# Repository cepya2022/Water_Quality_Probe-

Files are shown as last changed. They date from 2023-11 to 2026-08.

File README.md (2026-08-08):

# Water_Quality_Probe-

## Introduction

The development of open-source code and hardware instruments enables both the creation of new technologies and the redesign and adaptation of existing instruments to the user's specific needs. This allows free access to design and operational documentation, creating the possibility for the developed instruments to be replicated, assembled, studied, modified, shared, and collaboratively commercialized by anyone.

The current project involves the design of a low-cost multiparametric water quality probe that enables in situ and remote sensing of physicochemical variables relevant to the environment, such as conductivity, dissolved oxygen, temperature, and pH in bodies of water. The first prototype based on Arduino is already available, and efforts are underway to refine it in order to achieve a more robust, economical, and efficient product. This project proposes integrating the microcontroller into a single printed circuit board (PCB) that facilitates data acquisition and storage over extended periods, reduces energy consumption, and enhances robustness, considering its predominantly outdoor operation.

<p>
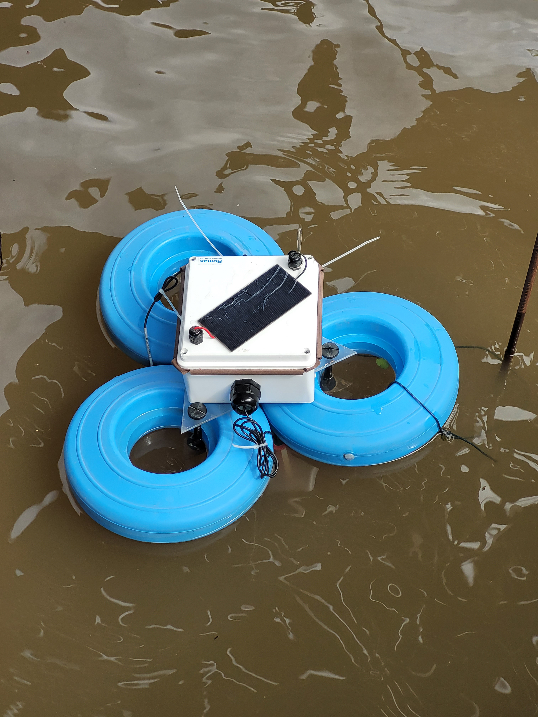
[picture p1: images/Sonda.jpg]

</p>

### Hardware

The monitoring station consists of a sealed waterproof box that floats with the assistance of auxiliary buoys. Inside the box, there is an Arduino Mega microcontroller connected to an external clock, an SD memory module, a low-energy Bluetooth module, a solar-powered energy system, and signal processing and decoupling systems for each sensor. Submersible cables extend from this box to the probes, allowing sampling in the water.

Regarding energy aspects, a solar-powered system was designed. It includes a Li-Ion battery (or two arranged in parallel) that powers the microcontroller and sensors, connected to a 1 Watt solar panel, providing indefinite energy autonomy.

Additionally, it integrates a Bluetooth device using 4.0 BLE (Bluetooth Low Energy) technology. The Serial Bluetooth Terminal® app enables remote control of the probe, such as remote power on/off, selection of measurement intervals, sensor calibration, and data query, curing, and collection. It's worth noting that each measurement includes the exact date and time it was taken. These features make it easy to remotely monitor many relevant variables over extended periods with high sampling rates, allowing for detailed time-series data collection at the study site.

<p align="center">
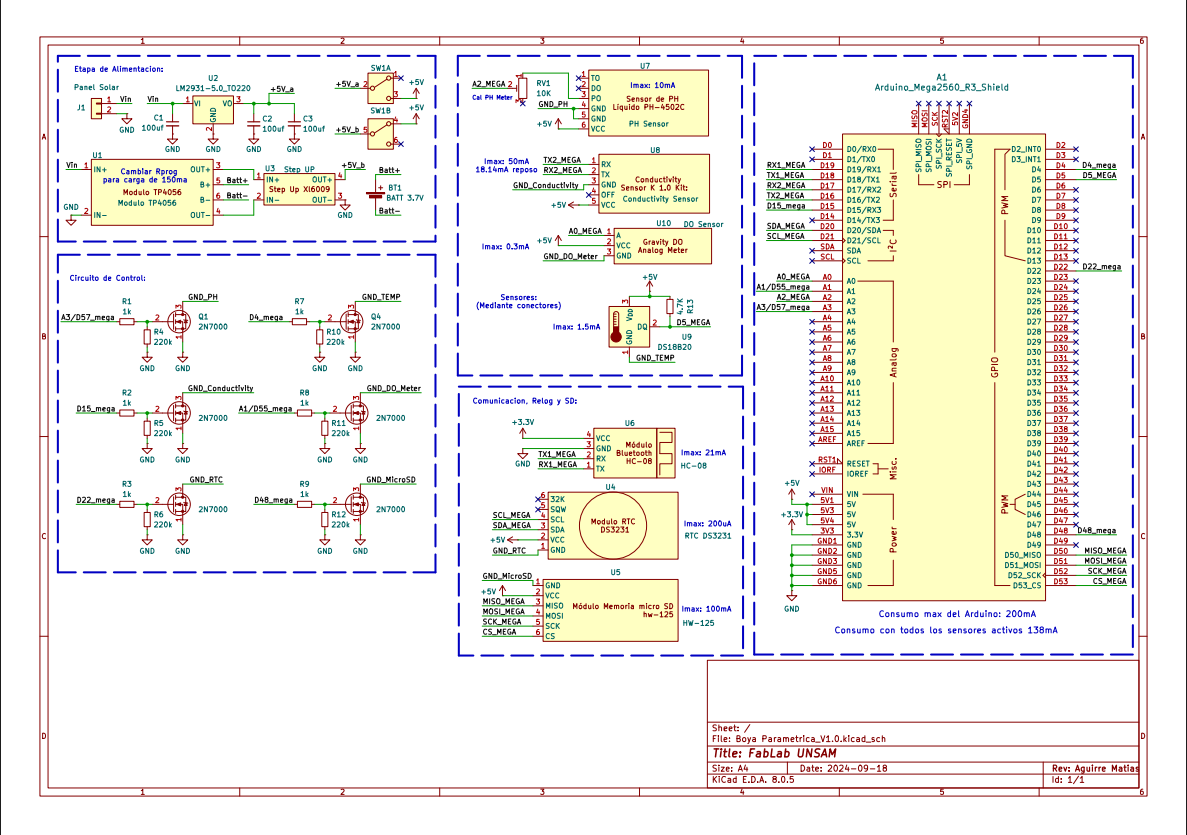
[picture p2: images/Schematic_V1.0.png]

</p>

#### Components

* Solar Panel
* Double battery holder
* Arduino Mega 2560 Rev3
* Step Up Power Supply Xl6009 Dc Adjustable Dc 5v 35v 3a Max Arduino
* Lithium Battery Charger Micro USB Module Tp4056 5v
* HC-08 BLE Bluetooth Module
* Micro SD Memory Reader Module: hw-125
* DS3231 RTC Clock
* DS18B20 Submersible Stainless Steel Digital Temperature Sensor
* PH-4502C Liquid PH Sensor with E201-BNC Electrode
* Conductivity Sensor Conductivity K 1.0 Kit (Atlas Scientific)
* Gravity™ Analog Dissolved Oxygen Meter Dissolved Oxygen Sensor (Atlas Scientific)
* 6x 2N7000 N-Channel MOSFETs (low-side power switching, one per module)
* Resistors (1 kΩ gate series, 220 kΩ gate pull-down, 1.7 kΩ OneWire pull-up)

Each sensor and peripheral (pH, conductivity, dissolved oxygen, temperature, RTC and SD card) has
its ground routed through its own 2N7000 MOSFET, so the microcontroller can power each module
independently. Driving the corresponding gate pin `HIGH` closes the low-side switch and powers the
module; `LOW` removes its ground reference and turns it off. Earlier prototypes used an
optocoupled relay module for this; the V1.0 PCB replaced it entirely with MOSFETs.

### Software

The research team is continuosly working on and improving the code. It is written in c++ programming language inside the Arduino IDE as it is the default language for arduino microcontrollers. The system was design to enter sleep mode inside the loop function while the `measurement` option is disabled or in between measurements. It includes an interruption function which is activated once a message is received via Bluetooth. This function wakes the system, executes the corresponding command and once it is finished, it enters the loop again. The different commands include turning on/off the measurement cycle and setting its frequency, sensor calibration, data query and current state information. The updated code is available [here](https://github.com/cepya2022/Water_Quality_Probe-/blob/main/Code_Water_Quality_Probe.ino).

#### Building the firmware

Target board: **Arduino Mega 2560**.

⚠️ **`do_grav.h` is not included in this repository**, so the sketch will not compile from a fresh
clone until the library that provides it is installed. It comes from Atlas Scientific's
**`atlas_gravity`** library (the `Gravity_DO` class used for the dissolved oxygen sensor). That
library is not published to the Arduino Library Manager — download it from Atlas Scientific's
GitHub and copy the `atlas_gravity` folder into your Arduino `libraries/` directory manually.

The following libraries are also required. All except `atlas_gravity` are available through the
Arduino IDE Library Manager:

| Library | Used for |
|---|---|
| `atlas_gravity` | dissolved oxygen sensor (`do_grav.h`) — **manual install, see above** |
| `RTClib` | DS3231 real time clock |
| `Low-Power` | sleep between measurements |
| `DallasTemperature` | DS18B20 temperature sensor |
| `OneWire` | DS18B20 bus |
| `Wire` | I²C (RTC) — bundled with the IDE |
| `SPI` | SD card bus — bundled with the IDE |
| `SD` | SD card — bundled with the IDE |

The conductivity module is driven over `Serial2` with plain text commands, so it needs no library.

Setting the clock: `corregirReloj()` is called from `setup()` but is left commented out. Uncomment
it, upload once while connected to a computer so the RTC picks up the compile-time timestamp, then
comment it out again and re-upload — otherwise the clock is reset to the compile time on every boot.

#### Measurement cycles

Once the measurment is set to `On`, the interface will ask the user to identify the location with an ID (`locationID`) which must be a number. Once it is provided, the arduino will save the `On` state along with the location ID and the current frequency (default is 15 seconds), in a .txt file inside the SD Card. This feature acts as a reassurance in case of a sudden shutdown and restart of the system or any kind of reboot. In this case, during the setup function of the arduino, this file is checked to seek the last state in which the system was operating. In case the measurement was `On`, it sets the frequency and the location ID to their previous states and starts the measurement cycle, otherwise it keeps the default values and enters the loop. The frequency intervals available in the current version are 15 seconds and 1, 5, 15 or 30 minutes. Usually, for outdoor measurements, 30 minutes is a reasonable interval considering battery consumption, solar exposure and a relatively high sampling rate compared to other sampling methods.

During the measurement cycle, the arduino powers each sensor on and off in turn, so that only the module being read draws current at any given moment. First it turns on the pH sensor (`pH`) and waits about 2 seconds for it to settle, then averages 10 consecutive analog samples taken 10 ms apart and converts that average to a pH value using the stored calibration line. Next is the temperature sensor (`T`), which is read once. Third is the conductivity sensor (`EC`), one of the most accurate and precise ones and the slowest per reading, so a single measurement is taken; the value returned by the module is temperature-compensated, which is why it must be read after the temperature. Along with conductivity, the module also returns total dissolved solids (`TDS`). Finally, the dissolved oxygen (`DO`) is read once. Once the parameters are measured, the current date and time are read from the RTC and the record is appended to a .txt file on the SD card as semicolon-separated values, in the order: `date`;`time`;`DO`;`EC`;`TDS`;`pH`;`T`;`locationID`.

> Note: earlier revisions of this document described a 3 minute pH stabilization wait, attributed to
> induction from the relay module, and a 10-reading average for every sensor. Both belong to the
> relay-based prototype and do not describe the current firmware — the V1.0 board has no relays, and
> only pH averages multiple samples. The paragraph above reflects what the code actually does.

#### Data query and state info

There are 3 types of data querys available. The first to refer to the data stored from the measurement cycles. One of them returns the entire information stored in the SD card inside the measurement file, while the other returns only the new information added since the last measurement data query. In case of a shutdown and restart of the system or any kind of reboot, the pointer of the file returns to the first line of the text file, so both queries will return the same information. The third type of data query refers to individual measurements of each sensor taken at real-time. This includes options for each of the 4 sensors and the RTC clock.

The current state information is also a query that returns wether the the measurement mode is On or Off, and the established frequency.

#### Sensor Calibration

The only sensor without the need of a calibration process is the Temperature one, the other three sensors have specific code and procedures for their correct calibrations. 

For the pH sensor, the calibration requires a pH=7 and a pH=4 standard solutions. First, the interface will request the user to use the pH=7 solution and press the `Ok` command when a stable condition is reached. It is recommended to wait at least 3 minutes until it reaches a stable electronic condition in each solution. Then, it will request to do the same in the pH=4 solution. Make sure to wash the probe with distilled water in between solutions. Once both solutions are used, the arduino will give the user the notification that the pH sensor is calibrated and it will save the calibration curve parameters, slope of curve (m) and intercept to the origin (O.o.), in the same file as the Location ID and the measurement state for it to be used in case of a sudden shutdown and restart of the system or any kind of reboot.

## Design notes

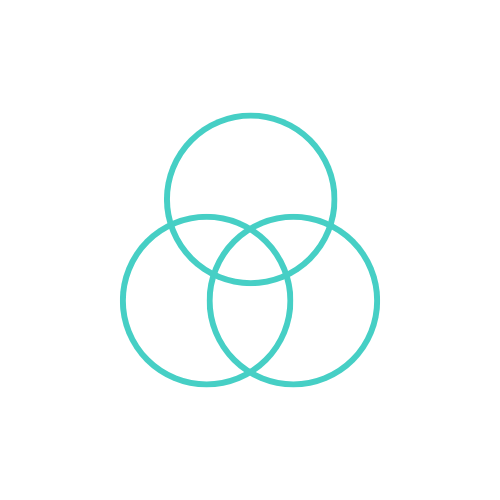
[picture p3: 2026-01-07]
flutter-app/assets/images/bg-w_no_sensa.png

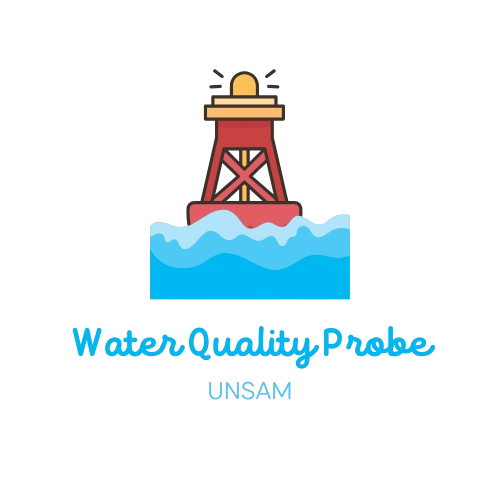
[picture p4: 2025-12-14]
flutter-app/flutter-app/assets/images/Water_Quality_Probe.png

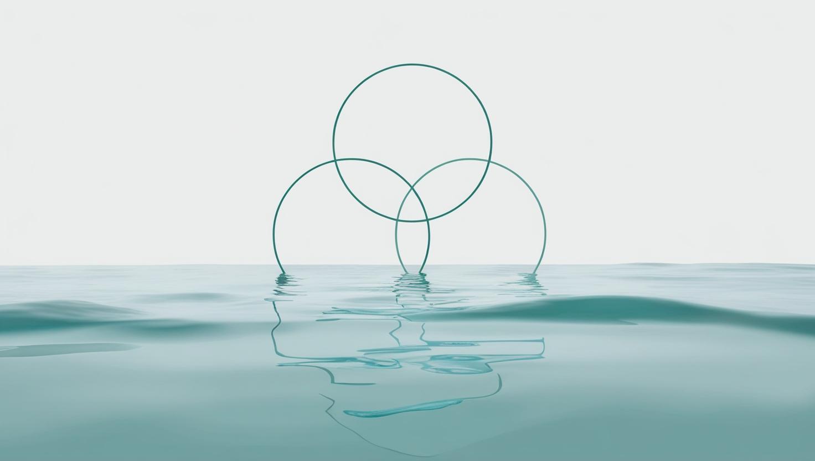
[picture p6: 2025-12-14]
flutter-app/assets/images/Circulos.jpg

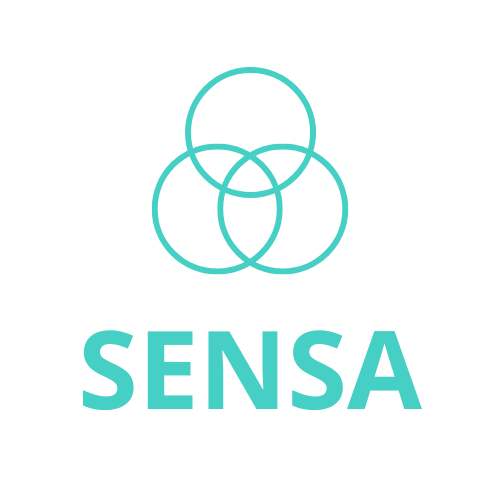
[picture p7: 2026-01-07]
flutter-app/assets/images/bg-w_sensa.png

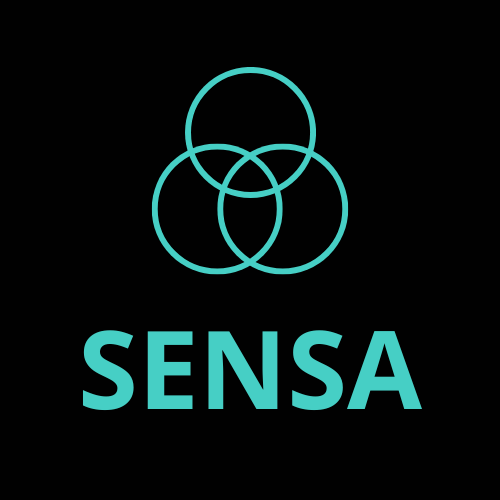
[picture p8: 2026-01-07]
flutter-app/assets/images/bg-b_sensa.png

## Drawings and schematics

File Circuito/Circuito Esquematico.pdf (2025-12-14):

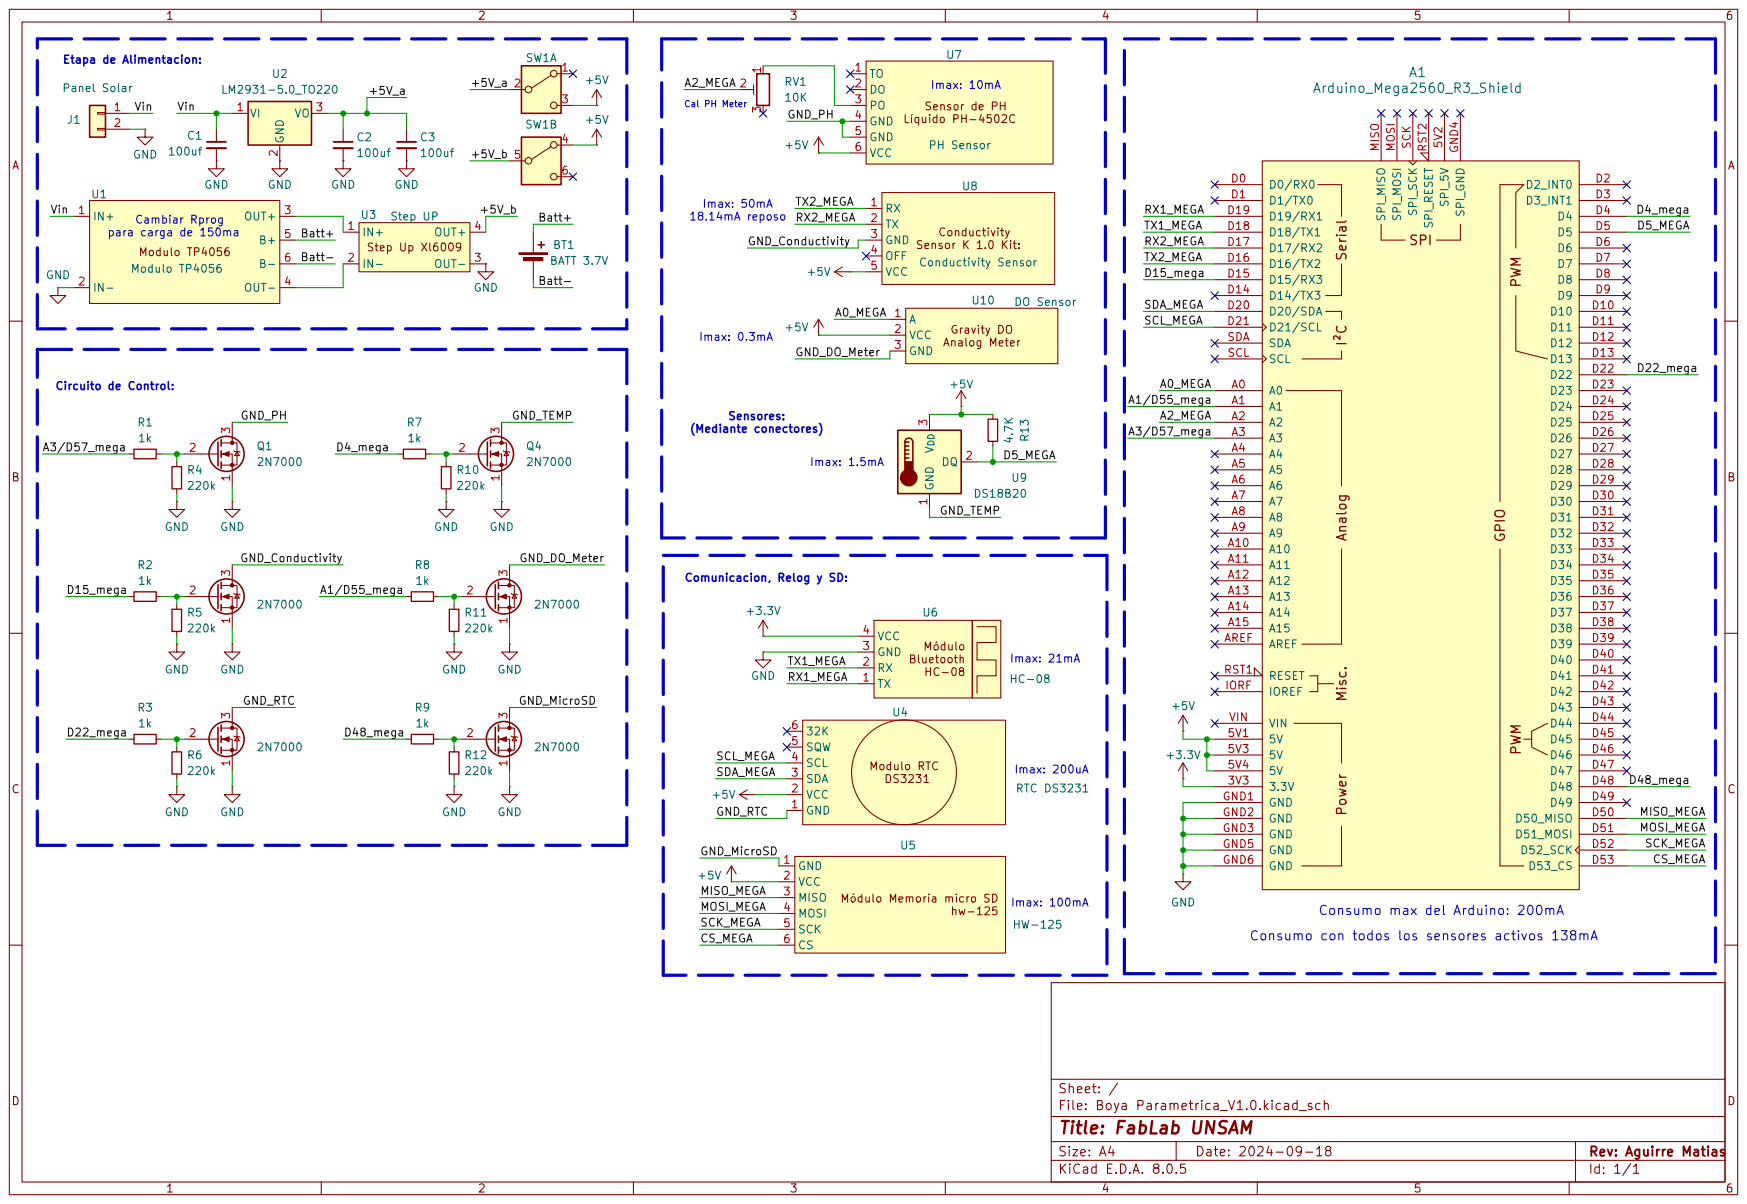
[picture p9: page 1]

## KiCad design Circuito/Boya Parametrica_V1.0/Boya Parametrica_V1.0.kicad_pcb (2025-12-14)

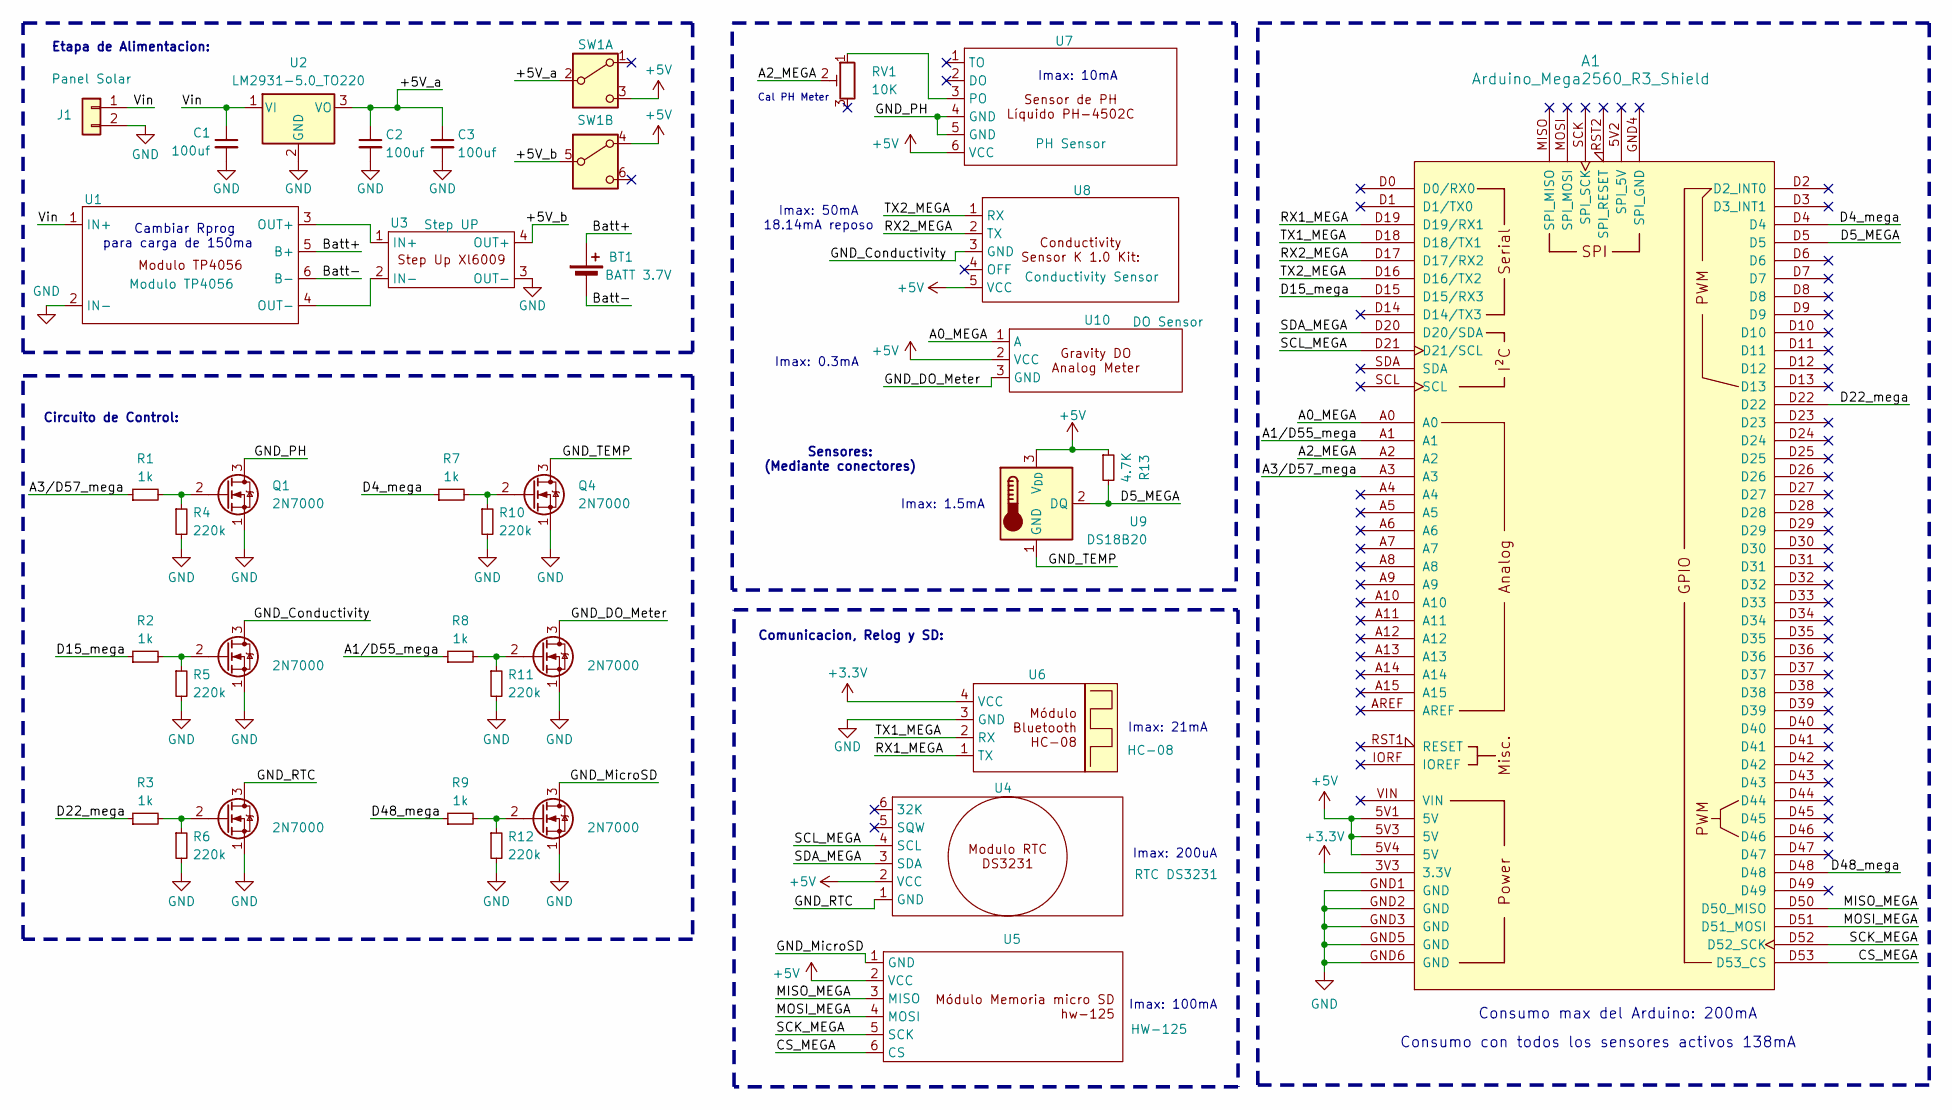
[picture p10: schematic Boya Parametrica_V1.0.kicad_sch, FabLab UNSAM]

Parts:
A1: Arduino_Mega2560_R3_Shield
BT1: BATT 3.7V; JST_EH_B2B-EH-A_1x02_P2.50mm_Vertical
C1, C2, C3: 100uf; C_Disc_D3.8mm_W2.6mm_P2.50mm
J1: Panel Solar; TerminalBlock_bornier-2_P5.08mm
Q1, Q2, Q3, Q4, Q5, Q6: 2N7000; TO-92L_Wide
R1, R2, R3, R7, R8, R9: 1k; R_Axial_DIN0204_L3.6mm_D1.6mm_P5.08mm_Horizontal
R4, R5, R6, R10, R11, R12: 220k; R_Axial_DIN0204_L3.6mm_D1.6mm_P5.08mm_Horizontal
R13: 4.7K; R_Axial_DIN0204_L3.6mm_D1.6mm_P5.08mm_Horizontal
RV1: 10K; Potentiometer_Bourns_3296W_Vertical
SW1: SW_CK_JS202011AQN_DPDT_Angled
U1: Modulo TP4056; TP4056-18650
U2: LM2931-5.0_TO220; TO-220-3_Vertical
U3: Step UP; hw-045
U4: RTC DS3231; RTC_DS3231
U5: HW-125; MICRO SD CARD HW-125
U6: HC-08; JST_EH_B4B-EH-A_1x04_P2.50mm_Vertical
U7: PH Sensor; JST_EH_B6B-EH-A_1x06_P2.50mm_Vertical
U8: Conductivity Sensor; JST_EH_B5B-EH-A_1x05_P2.50mm_Vertical
U9: DS18B20; JST_EH_B3B-EH-A_1x03_P2.50mm_Vertical
U10: DO Sensor; JST_EH_B3B-EH-A_1x03_P2.50mm_Vertical

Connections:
+3.3V: A1.3V3 (3.3V), U6.4 (VCC)
+5V: A1.5V1 (5V), A1.5V3 (5V), A1.5V4 (5V), R13.1, SW1.3 (C), SW1.4 (A), U4.2 (VCC), U5.2 (VCC), U7.6 (VCC), U8.5 (VCC), U9.3 (V_{DD}), U10.2 (VCC)
/+5V_a: C2.1, C3.1, SW1.2 (B), U2.3 (VO)
/+5V_b: SW1.5 (B), U3.4 (OUT+)
/A0_MEGA: A1.A0, U10.1 (A)
/A1/D55_mega: A1.A1, R8.1
/A2_MEGA: A1.A2, RV1.2
/A3/D57_mega: A1.A3, R1.1
/Batt+: BT1.1 (+), U1.5 (B+)
/Batt-: BT1.2 (-), U1.6 (B-)
/CS_MEGA: A1.D53 (D53_CS), U5.6 (CS)
/D4_mega: A1.D4, R7.1
/D5_MEGA: A1.D5, R13.2, U9.2 (DQ)
/D15_mega: A1.D15 (D15/RX3), R2.1
/D22_mega: A1.D22, R3.1
/D48_mega: A1.D48, R9.1
/GND_Conductivity: Q2.3 (D), U8.3 (GND)
/GND_DO_Meter: Q5.3 (D), U10.3 (GND)
/GND_MicroSD: Q6.3 (D), U5.1 (GND)
/GND_PH: Q1.3 (D), U7.4 (GND), U7.5 (GND)
/GND_RTC: Q3.3 (D), U4.1 (GND)
/GND_TEMP: Q4.3 (D), U9.1 (GND)
/MISO_MEGA: A1.D50 (D50_MISO), U5.3 (MISO)
/MOSI_MEGA: A1.D51 (D51_MOSI), U5.4 (MOSI)
/RX1_MEGA: A1.D19 (D19/RX1), U6.1 (TX)
/RX2_MEGA: A1.D17 (D17/RX2), U8.2 (TX)
/SCK_MEGA: A1.D52 (D52_SCK), U5.5 (SCK)
/SCL_MEGA: A1.D21 (D21/SCL), U4.4 (SCL)
/SDA_MEGA: A1.D20 (D20/SDA), U4.3 (SDA)
/TX1_MEGA: A1.D18 (D18/TX1), U6.2 (RX)
/TX2_MEGA: A1.D16 (D16/TX2), U8.1 (RX)
/Vin: C1.1, J1.1, U1.1 (IN+), U2.1 (VI)
GND: A1.GND1 (GND), A1.GND2 (GND), A1.GND3 (GND), A1.GND5 (GND), A1.GND6 (GND), C1.2, C2.2, C3.2, J1.2, Q1.1 (S), Q2.1 (S), Q3.1 (S), Q4.1 (S), Q5.1 (S), Q6.1 (S), R4.2, R5.2, R6.2, R10.2, R11.2, R12.2, U1.2 (IN-), U2.2 (GND), U3.3 (OUT-), U6.3 (GND)
unnamed: Q1.2 (G), R1.2, R4.1
unnamed: Q2.2 (G), R2.2, R5.1
unnamed: Q3.2 (G), R3.2, R6.1
unnamed: Q4.2 (G), R7.2, R10.1
unnamed: Q5.2 (G), R8.2, R11.1
unnamed: Q6.2 (G), R9.2, R12.1
unnamed: U1.3 (OUT+), U3.1 (IN+)
unnamed: U1.4 (OUT-), U3.2 (IN-)
unnamed: RV1.1, U7.3 (PO)

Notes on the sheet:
Circuito de Control:
Sensores: (Mediante conectores)
Imax: 0.3mA
Consumo con todos los sensores activos 138mA
Imax: 1.5mA
Consumo max del Arduino: 200mA
Imax: 21mA
Imax: 10mA
Etapa de Alimentacion:
Imax: 100mA
Imax: 50mA 18.14mA reposo
Cal PH Meter
Imax: 200uA
Comunicacion, Relog y SD:
Cambiar Rprog para carga de 150ma

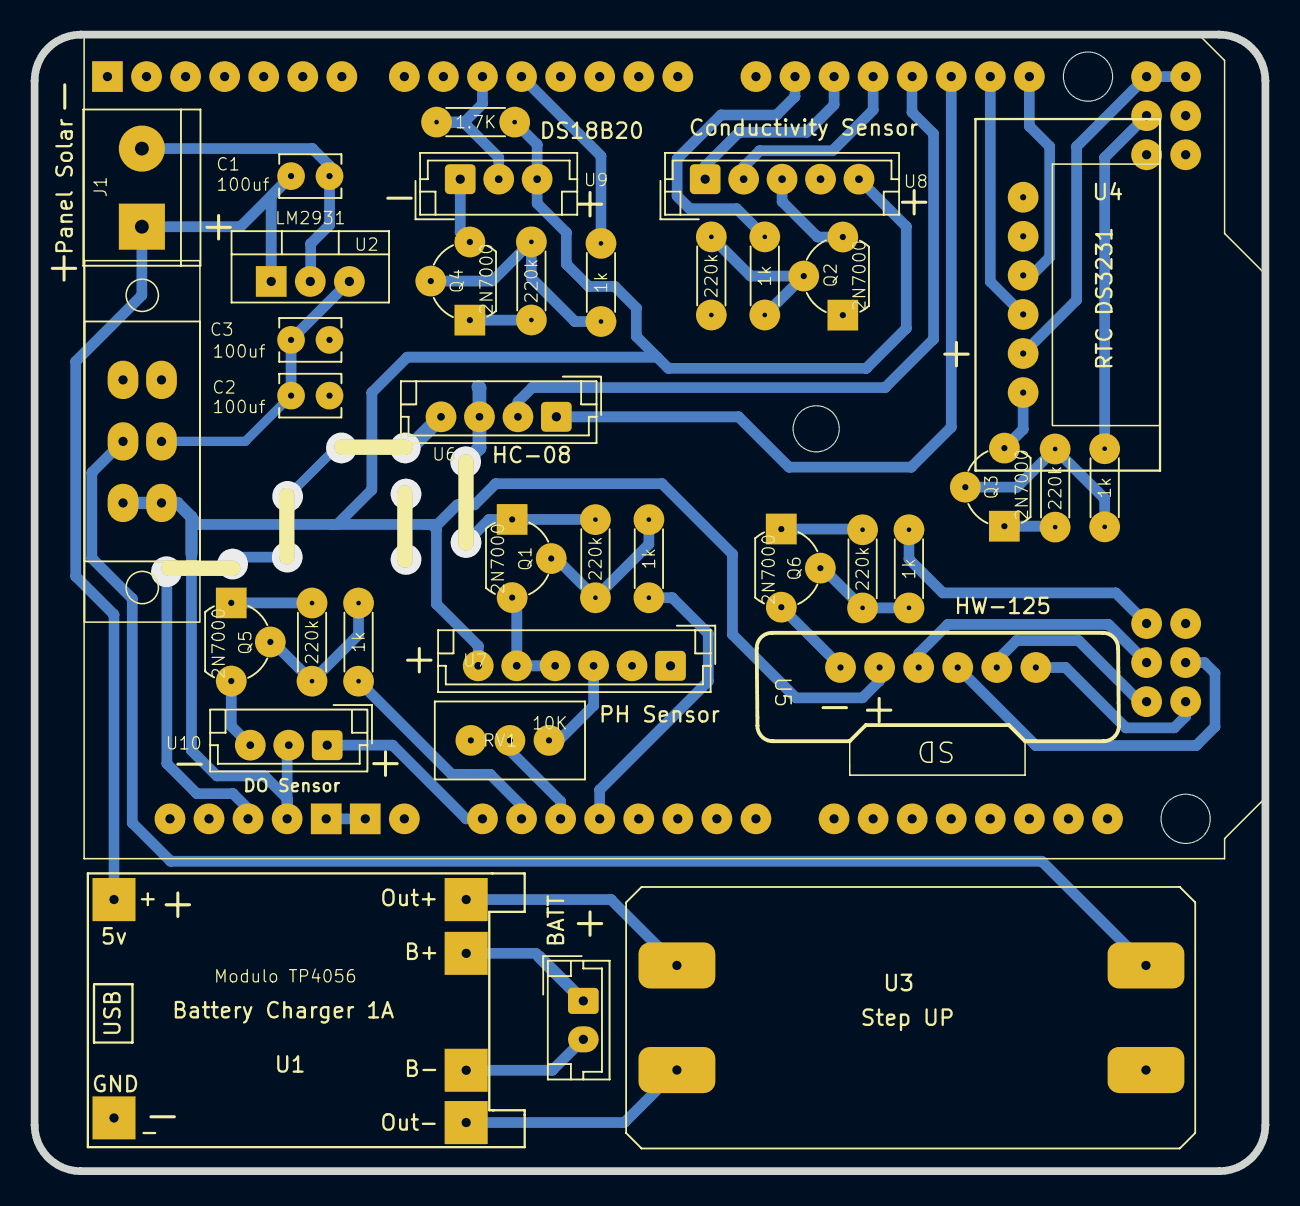
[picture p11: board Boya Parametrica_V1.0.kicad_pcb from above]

Board: 2 copper layers, 80.0 x 73.9 mm, 37 parts (0 on the bottom side), 42 nets.

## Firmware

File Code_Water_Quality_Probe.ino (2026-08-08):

#include <RTClib.h>
#include <LowPower.h>
#include <DallasTemperature.h>
#include <OneWire.h>
#include <Wire.h>
#include <SPI.h>
#include <SD.h>
#include "do_grav.h"

// Control de alimentacion: MOSFETs 2N7000 en low-side sobre el GND de cada modulo.
// Gate en HIGH -> conduce -> modulo alimentado. La placa V1.0 no lleva reles.
#define SensorTpin 5
#define bjtpH 57 // A3 o D57 son análogos
#define bjtOD 55 // A1 o D55 son análogos
#define bjtEC 15
#define bjtT 4
#define bjt_RTC 22
#define bjt_SD 48
#define SSpin 53

const unsigned long TIMEOUT_BT_MS = 300000UL; // 5 min de espera max por datos via BT antes de cancelar

// Modo de sueño entre mediciones. Ver dormirUnCiclo().
//   1 = idle      -> el reloj de I/O sigue activo, USART1 recibe mientras duerme:
//                    los comandos BT NO se pierden. Consume ~8-10 mA mas.
//   0 = powerDown -> consumo minimo, pero el USART queda sin reloj y se pierde
//                    todo byte que llegue durante el sueño.
#define SUENO_RECEPTIVO_BT 1

float volt, volt4, volt7; // medición y calibración de pH
float pendiente = -4.040; // nueva calibracion con boya 2.0
float ordenada = 22.600; // nueva calibracion con boya 2.0
unsigned long int avgval;
//int buffer_arr[10], temp;
float pH, T, OD; // guardan el valor de las variables FQ
// Variables escritas desde la interrupcion de BT y leidas en loop()/hacerAccion().
// Deben ser volatile para que el compilador no las cachee en registros: minutos es
// la via de escape del for de sueño y datobt corta los while de calibracion.
volatile char datobt;
volatile int minutos = 3; // frecuencia de medicion
int minprev;  // variable auxiliar
int contador = 0;
char ODon = 'b'; // prendido/apagado del sensor
char ECon = 'b'; // prendido/apagado del sensor
char pHon = 'b'; // prendido/apagado del sensor
char Ton = 'b'; // prendido/apagado del sensor
char eliminar = 'b'; // eliminar datos de la SD
volatile char medir = 'b';
char onprev = 'b';  // variable auxiliar
char calEC = 'b';  // calibración conductímetro
char calOD = 'b'; // calibración oxímetro
char calpH = 'b'; // calibración pH
char rectapH = 'b'; // variable auxiliar
char datosEC = 'b'; // enviar datos
char datosOD = 'b'; // enviar datos
char datospH = 'b'; // enviar datos
char datosT = 'b'; // enviar datos
char datosReloj = 'b'; // enviar datos
char enviar = 'b'; // enviar datos
volatile char cambioEstado = 'b'; // registra cambios en la configuracion
char consultarEstado = 'b'; // pide relectura/impresion del estado guardado en la SD
float punto1, punto2 = 0; // calibración conductímetro
float puntoStd = 12880; // calibración conductímetro
String fecha = ""; // valor de la fecha y hora actual
//float punto = 0; // pto de medición (nro. de estación, ubicación, id, etc)
String punto = ""; // pto de medición (nro. de estación, ubicación, id, etc)
String frecuencia = "";
volatile int pos;  // variable auxiliar
char titulo = 'b'; // variable auxiliar
char apagar = 'b';
String receivedString = ""; // variable auxiliar

String EC = "";                             //a string to hold the data from the Atlas Scientific product
String TDS = "";
String sensorstring = "";                             //a string to hold the data from the Atlas Scientific product

Gravity_DO DO = Gravity_DO(A0);
File datos;
File estadoprev;
RTC_DS3231 rtc;
DateTime dt (__DATE__, __TIME__);
OneWire oneWireObjeto(SensorTpin);
DallasTemperature sensorT(&oneWireObjeto); // para sensor DS18B20. Pasa referencia, no valor

void setup() {  
  apagarPines();
  delay(100);
  Serial1.begin(9600); //cambio a 9600 pq es un HC-06 (ORIGINAL 38400)
  delay(1000);
  attachInterrupt(digitalPinToInterrupt(19), interrupcionBT, RISING); // 19 xq en el mega Serial1 es 19 y 18 para TX y RX
  setearPines();
  delay(100);
  //Serial.begin(9600);
  //corregirReloj(); // COMENTAR UNA VEZ AJUSTADA Y VOLVER A SUBIR
  chequearEstado();
  delay(1000);
}

// Duerme un bloque de 4 s. Despierta antes si llega algo por BT.
void dormirUnCiclo(){
#if SUENO_RECEPTIVO_BT
  // SLEEP_MODE_IDLE: se detiene el CPU pero sigue el reloj de I/O, asi USART1
  // (Bluetooth, pines 18/19) recibe los bytes que lleguen durante el sueño.
  // IMPORTANTE: en modo idle CUALQUIER interrupcion habilitada despierta al MCU.
  // Por eso hay que apagar TODOS los timers: si TIMER0 queda encendido, su
  // desborde de ~1 ms (el de millis()) despertaria al equipo enseguida y esta
  // funcion volveria a los ~1 ms en lugar de a los 4 s, achicando el intervalo
  // de medicion unas 4000 veces. Asi solo despiertan el watchdog o el BT.
  LowPower.idle(SLEEP_4S, ADC_OFF,
                TIMER5_OFF, TIMER4_OFF, TIMER3_OFF, TIMER2_OFF, TIMER1_OFF, TIMER0_OFF,
                SPI_OFF,
                USART3_OFF, USART2_OFF, USART1_ON, USART0_OFF,
                TWI_OFF);
#else
  LowPower.powerDown(SLEEP_4S, ADC_OFF, BOD_OFF);
#endif
}

void loop() {
  if (cambioEstado == 'a'){
    guardarEstado();
  }
  delay(1000); // ver si puedo bajar este delay
  for (int i = 0; i < minutos; i++){
    dormirUnCiclo();
  }
  hacerAccion();
}

bool guardarPunto(){
  Serial1.flush();
  Serial1.println(F("Escribir punto de mediciones:"));
  delay(300);
  punto = "";
  delay(200);
  unsigned long t0 = millis();
  while (punto == "" || (int)punto[0] == 10){
    if (Serial1.available()){
      punto = Serial1.readStringUntil('\r');
    }
    if (millis() - t0 > TIMEOUT_BT_MS){
      Serial1.println(F("Tiempo de espera agotado, cancelando"));
      medir = 'b';
      titulo = 'b';
      cambioEstado = 'a';
      return false;
    }
  }
  //delay(100);
  Serial1.print(F("Nuevo punto: "));
  Serial1.println(punto);
  delay(500);
  Serial1.println(F("Indique frecuencia de medición:"));
  frecuencia = "";
  //while (frecuencia[0] != 'n' || frecuencia[0] != 'h' || frecuencia[0] != 'q' || frecuencia[0] != 't' || frecuencia[0] != 'o'){
  t0 = millis();
  while (frecuencia == ""){
    //frecuencia = "";
    if (Serial1.available()){
      frecuencia = Serial1.readStringUntil('\r');
    }
    if (millis() - t0 > TIMEOUT_BT_MS){
      Serial1.println(F("Tiempo de espera agotado, cancelando"));
      medir = 'b';
      titulo = 'b';
      cambioEstado = 'a';
      return false;
    }
  }
  delay(100);
  if (frecuencia[0] == 'n'){minprev = 3;}
  else if (frecuencia[0] == 'h'){minprev = 70;}
  else if (frecuencia[0] == 'q'){minprev = 216;}
  else if (frecuencia[0] == 'o'){minprev = 14;}
  else {minprev = 441;}
  delay(300);
  //Serial1.print(F("punto guardado: "));
  //Serial1.println(punto);
  Serial1.print(F("frecuencia de medición: "));
  Serial1.println(minprev/15);
  delay(200);
  guardarEstado();
  delay(100);
  //Serial1.println(F("a medir"));
  titulo = 'a';
  delay(100);
  return true;
}

void hacerTodo(){
  if (titulo == 'b'){
    if (!guardarPunto()){
      return;
    }
  }
  delay(500);
  Serial1.println(F("a medir"));
  delay(100);
  medirpH(0);
  delay(100);
  medirT();
  delay(100);
  medirEC();
  delay(100);
  medirOD();
  delay(100);
  obtenerFecha();
  delay(100);
  pegarDatosEnSD();
  //delay(100);
  //mostrarDatosEnSerial();
}

/*void mostrarDatosEnSerial(){
  Serial.print(fecha);
  Serial.print(';');
  Serial.print(OD);
  Serial.print(';');
  Serial.print(EC);
  Serial.print(';');
  Serial.print(pH);
  Serial.print(';');
  Serial.print(T);
  Serial.print(';');
  Serial.println(punto);
}*/

void medirOD(){
  digitalWrite(bjtOD, HIGH);
  delay(100);
  if(DO.begin()){
    //Serial.println(F("Loaded EEPROM"));
  }
  OD = DO.read_do_percentage(); 
  if (ODon == 'b'){
    digitalWrite(bjtOD, LOW);  
  }
}

void medirT(){
  digitalWrite(bjtT, HIGH);
  delay(100);
  sensorT.begin();
  sensorT.requestTemperatures();
  T = sensorT.getTempCByIndex(0);
  if (T == -127){
    Serial1.println(F("Error: sensor de T desconectado o fallo de lectura"));
  }
  delay(100);
  if (Ton == 'b'){
    digitalWrite(bjtT, LOW);
  }
}

void setearRectapH(){
  float pendienteAnterior = pendiente;
  float ordenadaAnterior = ordenada;
  Serial1.println(F("mandar valor de pendiente"));
  pendiente = 0;
  delay(100);
  unsigned long t0pH = millis();
  while (pendiente == 0){
    if (Serial1.available()){
      pendiente = Serial1.parseFloat();
    }
    if (millis() - t0pH > TIMEOUT_BT_MS){
      Serial1.println(F("Tiempo de espera agotado, cancelando"));
      pendiente = pendienteAnterior;
      ordenada = ordenadaAnterior;
      minutos = minprev;
      medir = onprev;
      rectapH = 'b';
      return;
    }
  }
  delay(100);
  Serial1.println(F("mandar valor de ordenada"));
  ordenada = 0;
  delay(100);
  t0pH = millis();
  while (ordenada == 0){
    if (Serial1.available()){
      ordenada = Serial1.parseFloat();
    }
    if (millis() - t0pH > TIMEOUT_BT_MS){
      Serial1.println(F("Tiempo de espera agotado, cancelando"));
      ordenada = ordenadaAnterior;
      minutos = minprev;
      medir = onprev;
      rectapH = 'b';
      return;
    }
  }
  delay(100);
  Serial1.println(F("recta de calibracion de pH seteada"));
  minutos = minprev;
  medir = onprev;
  rectapH = 'b';
  delay(100);
  guardarEstado();
  delay(200);
}

void calibrarPeachimetro(){
  digitalWrite(bjtpH, HIGH);
  delay(100);
  datobt = ' ';
  Serial1.println(F("poner sonda en sn standard 7 y apretar una vez boton OK"));
  delay(100);
  Serial1.println(F("recomendacion: esperar 3 min a que equilibre"));
  unsigned long t0 = millis();
  while(datobt != 'k'){
    if (Serial1.available()){
      datobt = Serial1.read();
      t0 = millis();
    }
    if (datobt == 'a'){
      break;
    }
    if (datobt == 'P'){
      mandarpH();
    }
    if (millis() - t0 > TIMEOUT_BT_MS){
      Serial1.println(F("Tiempo de espera agotado, cancelando"));
      datobt = 'a';
      break;
    }
  }
  switch(datobt){
    case 'k':
    medirpH(7);
    datobt = ' ';
    Serial1.println(F("poner sonda en sn standrad 4 y apretar una vez boton OK"));
    t0 = millis();
    while(datobt != 'k'){ // cambiar aca por datobt?
      if (Serial1.available()){
        datobt = Serial1.read();
        t0 = millis();
      }
      if (datobt == 'a'){
        break;
      }
      if (datobt == 'P'){
        mandarpH();
      }
      if (millis() - t0 > TIMEOUT_BT_MS){
        Serial1.println(F("Tiempo de espera agotado, cancelando"));
        datobt = 'a';
        break;
      }
    }
    switch (datobt){
      case 'k':
      medirpH(4);
      Serial1.println(F("pH-metro calibrado"));
      break;      
    
      case 'a':
      Serial1.println(F("de baja la calibracion"));
      break;
    }
    break;
    
    case 'a':
    Serial1.println(F("de baja la calibracion"));
    break;
  }
  minutos = minprev;
  medir = onprev;
  calpH = 'b';
  datospH = 'b';
  delay(100);
  digitalWrite(bjtpH, LOW);

  guardarEstado();
  delay(200);
}

void medirpH(int p){
  digitalWrite(bjtpH, HIGH);
  for (int i = 0; i < 2; i++){ // para que este 3 sec hasta medir
    delay(1000);    
  }
  avgval = 0;
  for (int i = 0; i < 10; i++)
  {
    avgval += analogRead(A2);
    delay(10);
  }
  volt = (float)avgval * 4.941 / 1023 / 10; // cambiar aca el 4.96. 
  //pH = pendiente * volt + ordenada;
  switch(p){
    case 0:
    pH = pendiente * volt + ordenada;
    delay(100);
    if (pHon == 'b'){
      digitalWrite(bjtpH, LOW);
    }
    break;
    
    case 4:
    volt4 = volt;
    pendiente = 3 / (volt7 - volt4);
    ordenada = 7 - (pendiente * volt7);
    break;

    case 7:
    volt7 = volt;
    break;    
  }
}

void mandarOD(){
  char ODonAnterior = ODon;
  ODon = 'a'; // mantener encendido durante las 10 lecturas, evitar ciclar el rele
  for (int i = 0 ; i < 10 ; i++){
    medirOD();
    Serial1.print(F("OD = "));
    Serial1.println(OD);
    delay(100);
  }
  ODon = ODonAnterior;
  if (ODon == 'b'){
    digitalWrite(bjtOD, LOW);
  }
  minutos = minprev;
  medir = onprev;
  datosOD = 'b';
  //datospH = 'a';
}
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
